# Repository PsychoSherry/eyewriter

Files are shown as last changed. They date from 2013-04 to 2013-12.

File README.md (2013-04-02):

# Eyewriter

A DIY, open-source remote eye tracking toolkit meant to enable artistic digital expression for artists and students with diverse needs. 

This repo contains all of the source files necessary to fabricate and program the electronics system, as well as fabricate an adjustable 3D-printable platform that can be clamped onto any laptop or set on a table.

#### This repo contains:
* 3D files = all of the OpenSCAD scripts (and rendered STLs) for all of the 3D-printable files.
* Arduino sketches = sketches that can be loaded onto the electronics platform.
* BOMs = bills of materials for all required parts for the project.
* Eagle files = design files for all of the electronics modules
* oF app = openFrameworks program to translate camera data into usable actions

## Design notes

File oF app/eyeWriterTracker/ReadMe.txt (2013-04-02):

README 7/20/2010 by ito + kyle
EyeWriter Remote Eye Tracker

To use this realtime eye tracking system, you need a camera and IR LEDs and some electronics hardware.
For information on the hardware, please see (for now):
http://collab.eyewriter.org/?p=123
http://collab.eyewriter.org/?p=102

to use PSEYE USB camera with this software, we recommend to use the newest macam driver.
the macam driver can be downloaded from 
http://sourceforge.net/projects/webcam-osx/files/cvs-build/2009-09-25/macam-cvs-build-2009-09-25.zip/download

Arduino code for driving the hardware is at /StrobeEye/StrobeEye.pde

This software is made with Open Frameworks and based on the original EyeWriter software.
For more information about Open Frameworks and the Eye Writer project please see:
http://www.openframeworks.cc/
http://www.eyewriter.org/

To compile the code, the following openFrameworks addons are needed:
- ofxDirList
- ofxVectorMath
- ofxXmlSettings

Note:

To change the input mode to camera input (movie file input is chosen by default),
change the line 5 of (PROJECT FOLDER)/bin/data/Settings/inputSettings.xml as below.
from:   <mode>1</mode>
to:      <mode>0</mode>

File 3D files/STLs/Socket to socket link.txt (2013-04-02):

 
Cost
Machine time cost is 0.0$.
Material cost is 0.2$.
Total cost is 0.2$.
 
Extent
X axis extrusion starts at -15 mm and ends at 15 mm, for a width of 29 mm.
Y axis extrusion starts at -11 mm and ends at 11 mm, for a depth of 22 mm.
Z axis extrusion starts at 0 mm and ends at 33 mm, for a height of 33 mm.
 
Extruder
Build time is 12 minutes 57 seconds.
Distance extruded is 43078.2 mm.
Distance traveled is 53793.4 mm.
Extruder speed is 40.0
Extruder was extruding 80.1 percent of the time.
Extruder was toggled 4748 times.
Operating flow rate is 7.1 mm3/s.
Feed rate average is 69.2 mm/s, (4152.4 mm/min).
 
Filament
Cross section area is 0.089 mm2.
Extrusion diameter is 0.34 mm.
Volume fraction is 0.82.
 
Material
Mass extruded is 4.1 grams.
Volume extruded is 3.8 cc.
 
Meta
Text has 89122 lines and a size of 3129.0 KB.
Version is 12.03.14
 
Procedures
carve
preface
inset
fill
speed
raft
jitter
comb
cool
dimension
alteration
 
Profile
ABS
 
Slice
Edge width is 0.4 mm.
Layer height is 0.27 mm.

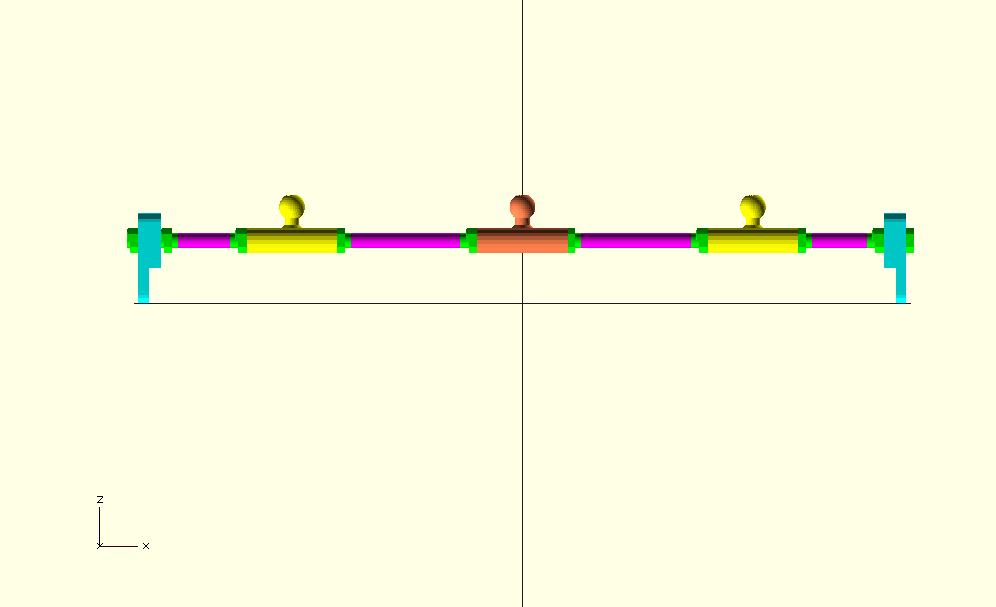
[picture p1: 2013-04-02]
3D files/Full mockup - front.png

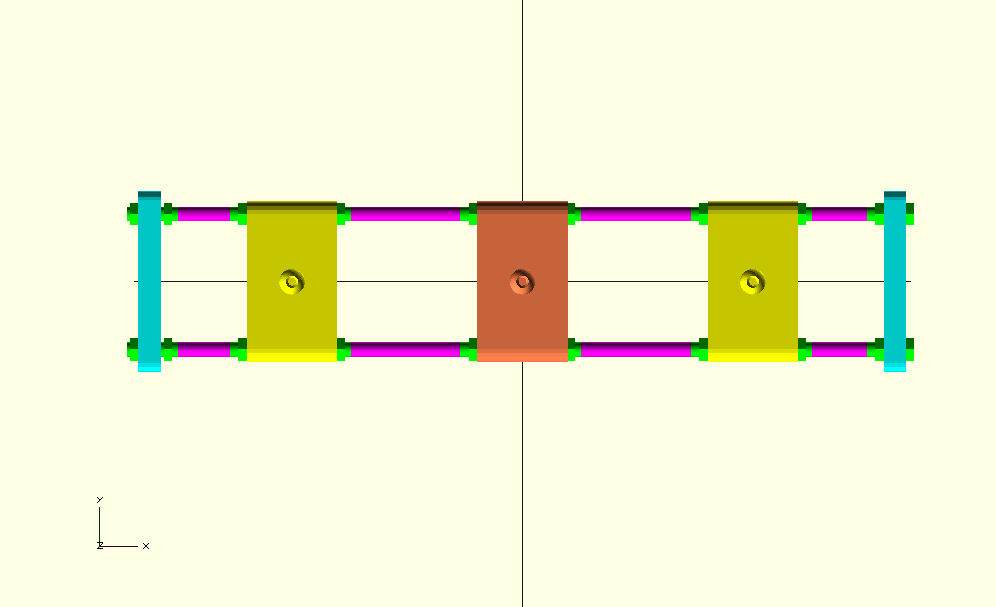
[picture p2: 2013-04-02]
3D files/Full mockup - top.png

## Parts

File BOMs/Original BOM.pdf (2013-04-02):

## Parts List

category | model number | shop | unit price | | total | URL
Camera | PS3Eye | Amazon | $32.00 | 1 | $32 | http://www.amazon.com/PlayStation-Eye-3/dp/B000VTQ3LU
M12 LENS | Board Lens (25 mm) | surveillance-video | $18.00 | 1 | $18 | http://www.surveillance-video.com/bole25mmform.html
M12 LENS holder | cmt-107 | optics-online | $6.00 | 1 | $6.00 | http://www.optics-online.com/
IR Filter | LEE FILTERS 87 100mm x 100mm | B&H (or others) | $13.95 | 1 | $13.95 | http://www.bhphotovideo.com/c/product/102762-REG/LEE_Filters_87P3_3x3_Infra_Red_87.html
IR LED | HSDL-4220 (516-1261-ND) | Digikey | $0.75 | 36 | $27 | http://www.digikey.com/
MOSFET | IRL3714ZPBF (IRL3714ZPBF-ND) | Digikey | $1.41 | 2 | $2.82 | http://www.digikey.com/
Regulator | MC7805ABTG(MC7805ABTGOS-ND) | Digikey | $0.67 | 1 | $0.67 | http://www.digikey.com/
Resistor 3.0OHM 1W | ERX-1SJ3R0 (P3.0W-1BK-ND) | Digikey | less than $1 | 2 | $1.00 | http://www.digikey.com/
Resistor 120OHM 1/4W | ERD-S2TJ121V (P120BACT-ND) | Digikey | less than $1 | 1 | $1.00 | http://www.digikey.com/
Resistor 1kOHM 1/4W | ERD-S2TJ102V (P1.0KBACT-ND) | Digikey | less than $1 | 1 | $1.00 | http://www.digikey.com/
Power Adaptor 7.5V | SPU10-103(7.5V, SPU1010375255595-ND) | Digikey | $14.84 | 1 | $14.84 | http://www.digikey.com/
Transistor | 2N2222 | RadioShack | $0.79 | 1 | $0.79 | http://www.radioshack.com/product/index.jsp?productId=2062608
Potentiometer | Rheostat(25Ohm - 3W) | RadioShack | $3.99 | 2 | $7.98 | http://www.radioshack.com/product/index.jsp?productId=2062299
Arduino | - | SparkFun | $29.95 | 1 | $29.95 | http://www.sparkfun.com/commerce/product_info.php?products_id=666
Male pin for Arduino female pin | Break Away Headers - Straight | SparkFun | $2.50 | 1 | $2.50 | http://www.sparkfun.com/commerce/product_info.php?products_id=116
Visible LED | Red LED | SparkFun | $0.35 | 1 | $0.35 | http://www.sparkfun.com/commerce/product_info.php?products_id=533
USB Cable for Arduino | - | SparkFun | $3.95 | 1 | $3.95 | http://www.sparkfun.com/commerce/product_info.php?products_id=512
BreadBoard | - | SparkFun | $5.95 | 1 | $5.95 | http://www.sparkfun.com/commerce/product_info.php?products_id=9567
Round PCB Kit (5-Pack) | - | RadioShack | $4.99 | 2 | $9.98 | http://www.radioshack.com/product/index.jsp?productId=3173937
Wire | - | RadioShack | $7.69 | 1 | $7.69 | http://www.radioshack.com/product/index.jsp?productId=2062656
Wire(30 Gauge for VSYNC) | - | RadioShack | $3.99 | 1 | $3.99 | http://www.radioshack.com/product/index.jsp?productId=2062642
Solder | thin solder is better.

Soldering Iron

Drill Press

Scissors

Screw Driver

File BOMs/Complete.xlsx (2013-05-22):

R1 | 10k | 0805 | 4 | $0.10 | $0.40 | P10KACT-ND | http://www.digikey.com/product-detail/en/ERJ-6GEYJ103V/P10KACT-ND/43118
R2-R5 | 39ohm | 1W power resistor | 8 | $0.34 | $2.72 | P39W-1BK-ND | http://www.digikey.com/product-detail/en/ERG-1SJ390/P39W-1BK-ND/35788
R6-R8 | 220ohm | 0805 | 3 | $0.10 | $0.30 | P220ACT-ND | http://www.digikey.com/product-detail/en/ERJ-6GEYJ221V/P220ACT-ND/90021
R9 | 100ohm | 0805 | 1 | $0.10 | $0.10 | P100ACT-ND | http://www.digikey.com/product-detail/en/ERJ-6GEYJ101V/P100ACT-ND/21875
R13 | 89ohm | 0805 | 1 | $0.10 | $0.10 | P82ACT-ND | http://www.digikey.com/product-detail/en/ERJ-6GEYJ820V/P82ACT-ND/42830
R14-R15 | 10k | Panel mount pot | 2 | $1.05 | $2.10 | P3A1103-ND | http://www.digikey.com/product-detail/en/EVU-F3AF30B14/P3A1103-ND/243597
C1 | 1uF | 0805 | 1 | $0.10 | $0.10 | 445-3463-1-ND | http://www.digikey.com/product-detail/en/C2012Y5V1H105Z%2F0.85/445-3463-1-ND/1801562
C2-C4 | 0.1uF | 0805 | 3 | $0.10 | $0.30 | 445-7534-1-ND | http://www.digikey.com/product-detail/en/C2012X7R1H104K085AA/445-7534-1-ND/2733606
C5 | 10uF | 1206 | 1 | $0.44 | $0.44 | 493-4147-1-ND | http://www.digikey.com/product-detail/en/F931C106KAA/493-4147-1-ND/2529874
Q1-Q3 | DMN3404L | SOT-23-3 | 3 | $0.45 | $1.35 | DMN3404LDICT-ND | http://www.digikey.com/product-detail/en/DMN3404L-7/DMN3404LDICT-ND/2052805
Q4 | MMBT2222A | SOT-23-3 | 1 | $0.14 | $0.14 | MMBT2222A-FDICT-ND | http://www.digikey.com/product-detail/en/MMBT2222A-7-F/MMBT2222A-FDICT-ND/815723
U1 | ATMEGA328P | 32-TQFP | 1 | $3.05 | $3.05 | ATMEGA328P-AU-ND | http://www.digikey.com/product-detail/en/ATMEGA328P-AU/ATMEGA328P-AU-ND/1832260
Y1 | 16MHz | 3-SMD | 1 | $0.48 | $0.48 | 490-1198-1-ND | http://www.digikey.com/product-detail/en/CSTCE16M0V53-R0/490-1198-1-ND/584635
LED1-LED16 | 940nm IR | 5mm (T 1 3/4) | 32 | $0.36 | $11.56 | 751-1204-ND | http://www.digikey.com/product-detail/en/TSAL6200/751-1204-ND/1681339
LED17 | Green LED | 0805 | 1 | $0.08 | $0.08 | 475-1410-1-ND | http://www.digikey.com/product-detail/en/LG%20R971-KN-1-0-20-R18/475-1410-1-ND/1802598
J1-J2 | 2-pin JST female | SMD R/A | 4 | $0.56 | $2.24 | 455-1749-1-ND | http://www.digikey.com/product-detail/en/S2B-PH-SM4-TB(LF)(SN)/455-1749-1-ND/926846?cur=USD
2-pin JST male plug |  |  | 4 | $0.12 | $0.48 | 455-1592-ND | http://www.digikey.com/product-detail/en/GHR-02V-S/455-1592-ND/807814
26-30AWG crimp contacts |  |  | 8 | $0.11 | $0.88 | 455-1606-1-ND | http://www.digikey.com/product-detail/en/SSHL-002T-P0.2/455-1606-1-ND/1642795
 |  |  |  | Total | $26.82
 |  |  |  |  | 26.82

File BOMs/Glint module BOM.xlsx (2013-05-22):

ID | Value | Package | Qty | Cost | Total | Part number | Source
R1-R2 | 39ohm | 1W power resistor | 2 | $0.34 | $0.68 | P39W-1BK-ND | http://www.digikey.com/product-detail/en/ERG-1SJ390/P39W-1BK-ND/35788
LED1-LED8 | 940nm IR | 5mm (T 1 3/4) | 8 | $0.36 | $2.89 | 751-1204-ND | http://www.digikey.com/product-detail/en/TSAL6200/751-1204-ND/1681339
J1-J2 | 2-pin JST female | SMD R/A | 1 | $0.56 | $0.56 | 455-1749-1-ND | http://www.digikey.com/product-detail/en/S2B-PH-SM4-TB(LF)(SN)/455-1749-1-ND/926846?cur=USD
 |  |  |  | Total | $4.13

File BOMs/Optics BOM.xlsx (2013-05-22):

Name | Specifications | Cost | S&H | Total | Part number | Source
PS3Eye camera | Modified for VSYNC and M12 lenses | $22.00 | $0.00 | $22.00 |  | http://www.amazon.com/Sony-PlayStation-Eye-Camera-Bulk-Packaging/dp/B0072I2240
M12x0.5 mount | 18mm hole spacing | $3.00 | $6.82 | $9.82 |  | http://www.m12lenses.com/Plastic-M12-Lens-Holder-p/pt-lh008p.htm
 | -- or -- 3D-printable | $0.00 | $0.00 | $0.00 |  | http://www.thingiverse.com/thing:83754?save=success
25mm M12 lens |  | $13.23 | $6.38 | $19.61 |  | http://www.m12lenses.com/ProductDetails.asp?ProductCode=PT-2520&CartID=1
IR filter | Band-pass filter (940nm) | $24.00 | $11.20 | $35.20 |  | http://peauproductions.com/store/index.php?main_page=product_info&cPath=2_12&products_id=23
 | -- or -- High-pass filter | $5.00 | $11.20 | $16.20 |  | http://peauproductions.com/store/index.php?main_page=product_info&cPath=2_12&products_id=88
 | -- or -- DIY filter (floppy disk, VHS, exposed film) | $0.00 | $0.00 | $0.00
#000-120x1/4" screws | Only needed for 3D-printed M12 mount. | $6.38 | $0.00 | $6.38 | 92482A147 | McMaster-Carr

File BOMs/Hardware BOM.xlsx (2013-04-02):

Part | Needed | Qty | Cost | P/N | Source
M8 threaded rod | 2 x ~500mm | 1m | $2.27 | 98861A080 | McMaster-Carr
M8 nut | 20 | 100 | $4.51 | 90592A022 | McMaster-Carr
M3 nut | 3 | 100 | $1.04 | 90592A009 | McMaster-Carr
M3x14 bolt | 3 | 100 | $4.24 | 92005A124 | McMaster-Carr
 |  | Total | $12.06

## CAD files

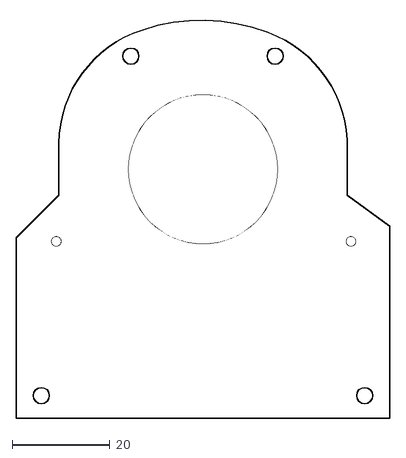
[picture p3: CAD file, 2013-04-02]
3D files/Board outlines/Main-Board.dxf
76.2 x 82.1

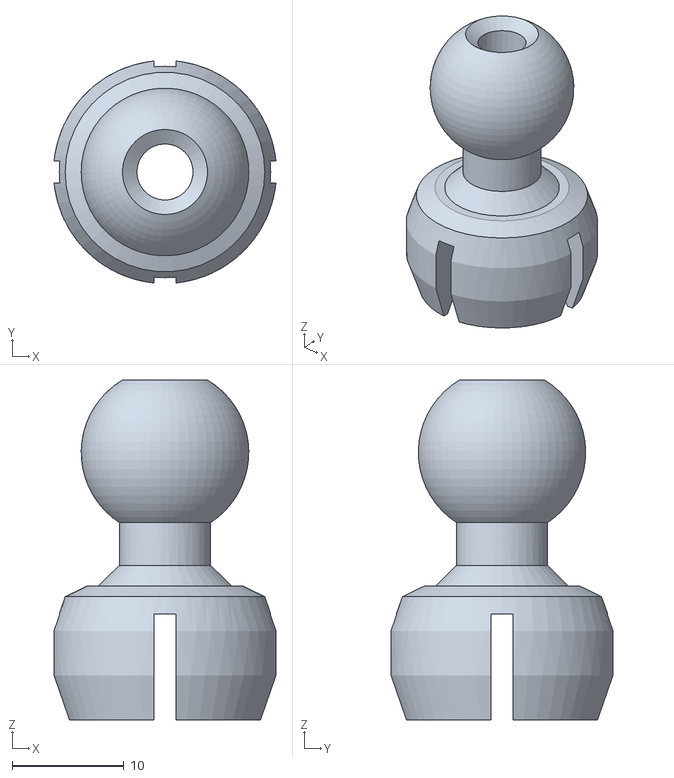
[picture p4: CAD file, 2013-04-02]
3D files/ball-and-socket.stl
19.9 x 19.9 x 30.5

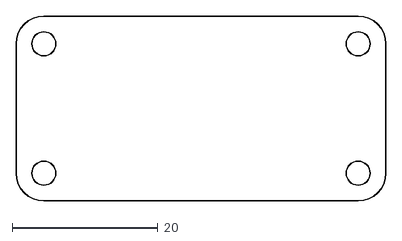
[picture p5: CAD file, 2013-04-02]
3D files/Board outlines/Glint-Module.dxf
50.8 x 25.4

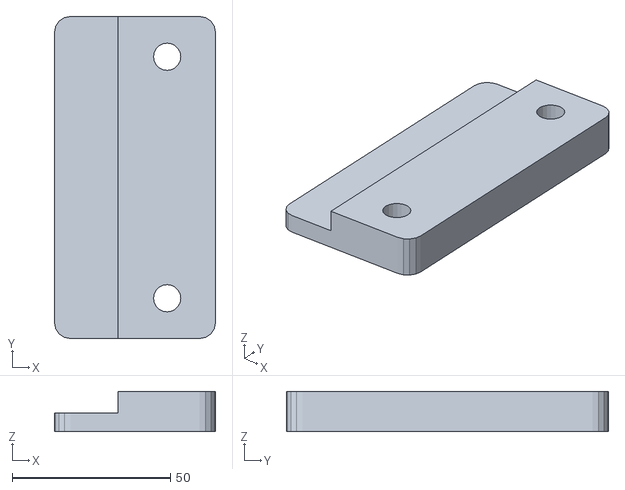
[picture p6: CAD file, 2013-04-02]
3D files/STLs/End block.stl
50.8 x 101.6 x 12.7

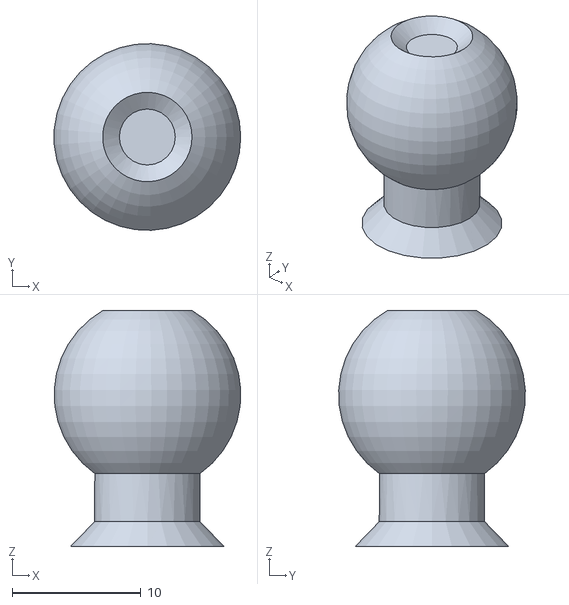
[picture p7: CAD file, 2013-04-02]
3D files/ball.stl
14.5 x 14.5 x 18.3

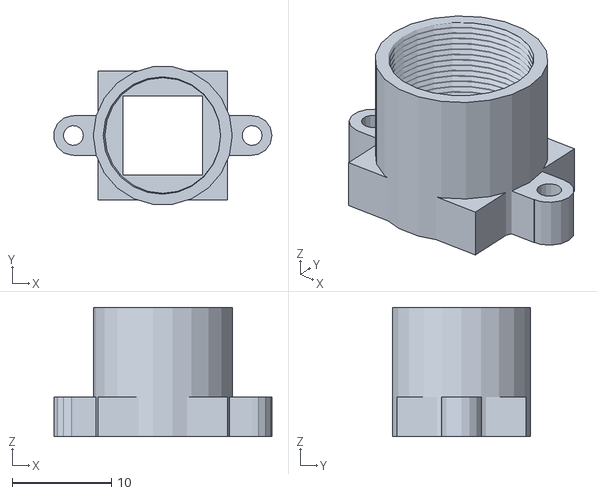
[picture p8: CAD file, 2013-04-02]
3D files/STLs/M12 mount.stl
22.0 x 13.9 x 13.0

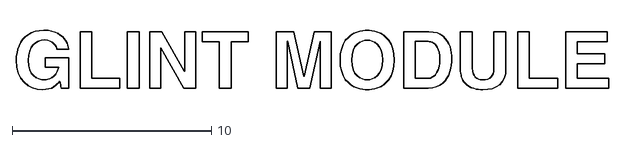
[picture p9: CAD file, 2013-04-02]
3D files/Board outlines/Glint module text.dxf
29.7 x 2.99

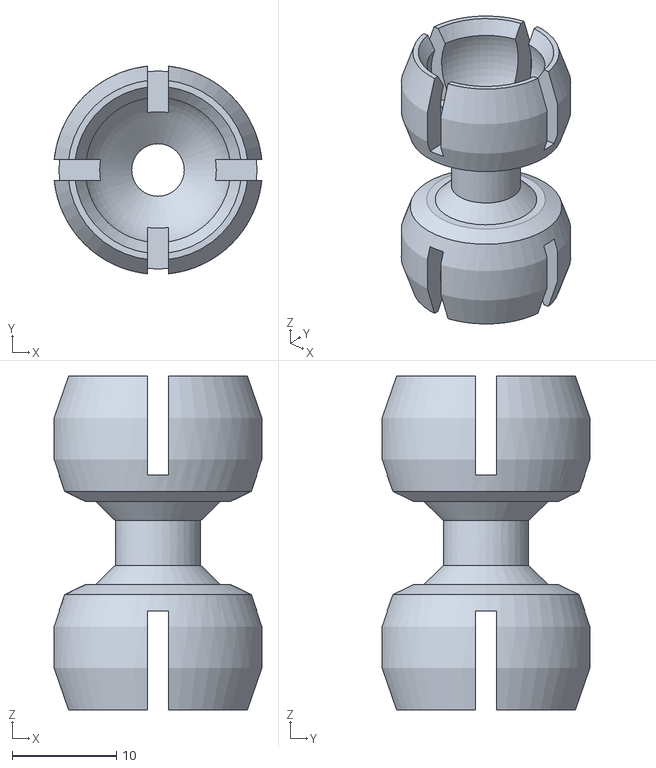
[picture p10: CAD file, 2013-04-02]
3D files/STLs/Socket to socket link.stl
19.9 x 19.9 x 32.0

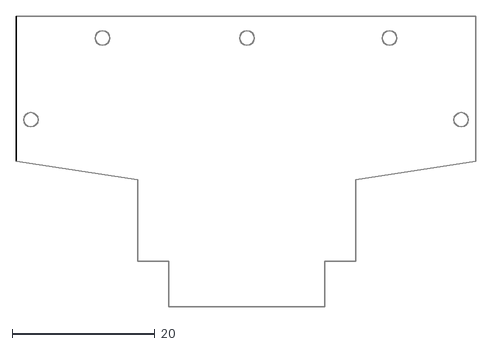
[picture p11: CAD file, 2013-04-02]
3D files/Board outlines/PS3Eye.dxf
64.3 x 40.6

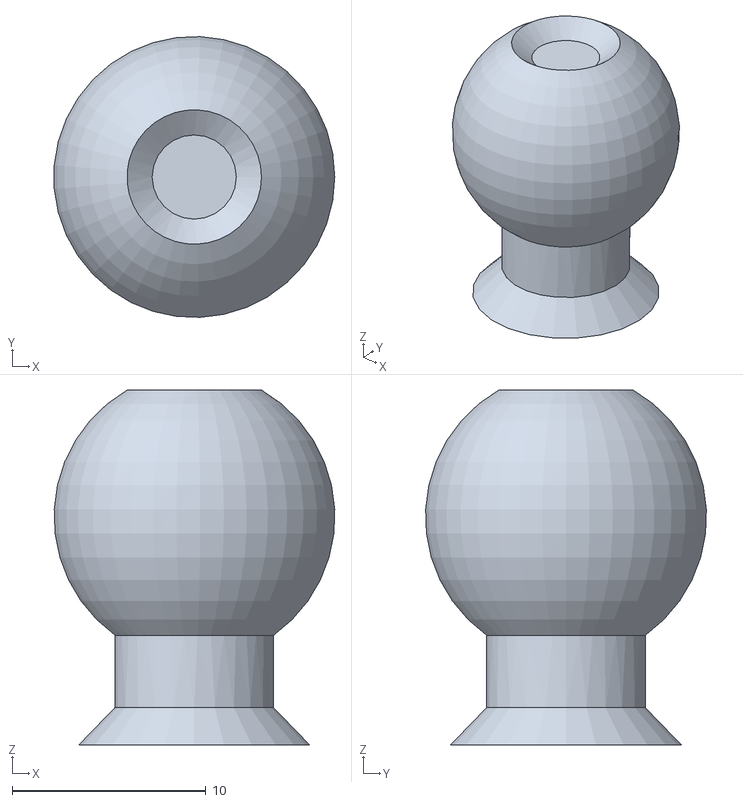
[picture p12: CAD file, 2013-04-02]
3D files/STLs/Modified ball.stl
14.5 x 14.5 x 18.3

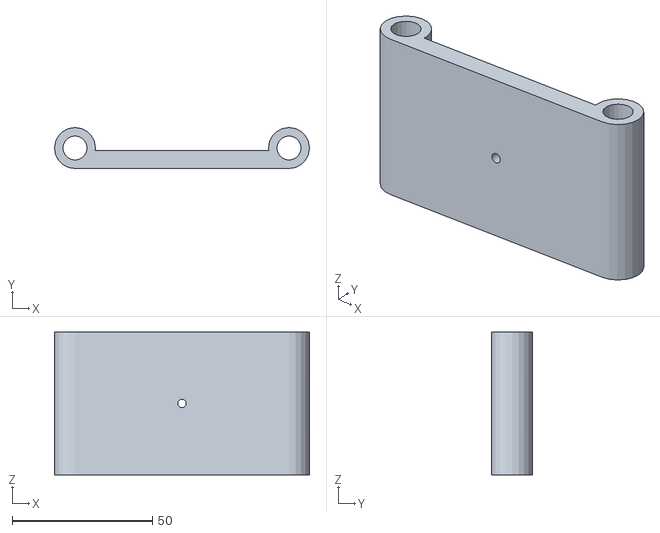
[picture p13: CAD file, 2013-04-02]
3D files/STLs/Platform.stl
90.8 x 14.6 x 50.8

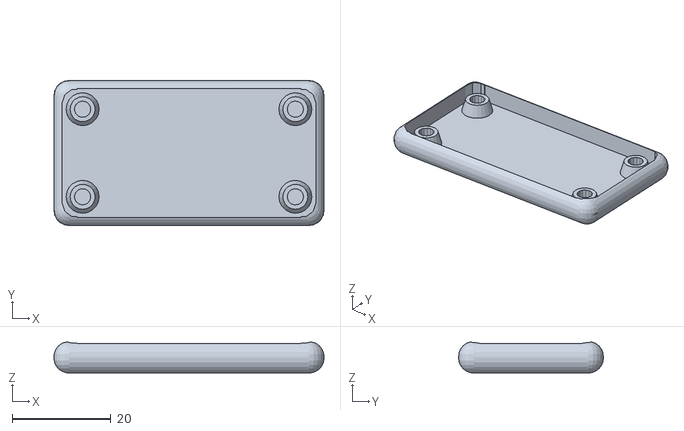
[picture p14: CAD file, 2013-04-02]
3D files/STLs/Glint module housing.stl
54.8 x 29.4 x 6.27

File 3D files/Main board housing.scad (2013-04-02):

include <lib/units.scad>
include <lib/boxes.scad>

housingDepth = 12;

boardWidth = 3*inch;
boardHeight = 3.2*inch;
boardThickness = 1.4;

// Spacer parameters
spacerHeight = .25*inch;
spacerOD = 2;
spacerID = 1;

showMainPCB = false;
showSpacers = true;
showPS3Eye = true;

difference() {
	translate([boardWidth/2, boardHeight/2, housingDepth/2])
		roundedBox([boardWidth + 3, boardHeight + 3, housingDepth], 5, false);
	
	translate([-3,-3,7])
		cube([boardWidth + 5, boardHeight + 5, 5]);

	translate([2.8*inch, 2.5*inch, 0])
		rotate([0,0,180])
			linear_extrude(height = 10)
				import("Board outlines/PS3Eye.dxf");
}

translate([boardWidth/2, boardHeight*2/3 - 3.5, boardThickness])
	color([1,1,1])
		cylinder(r = 12.5, h = 10);


// PS3Eye PCB
module ps3eye() {
	translate([2.8*inch, 2.5*inch, 0])
		rotate([0,0,180])
			linear_extrude(height = boardThickness)
				import("Board outlines/PS3Eye.dxf");
}

// Main PCB
module mainPCB() {
	translate([0,0, spacerHeight + boardThickness]) {
		color([0,1,1]) {
			difference() {
				linear_extrude(height = boardThickness)
					import("Board outlines/Main-Board.dxf");
				
				// Camera lens hole
				translate([1.5*inch, 2*inch, -.1])
					cylinder(r = .6*inch, h = 1.6);
		
				// Left PS3Eye standoff
				translate([.32*inch, 1.42*inch, 0])
					cylinder(r = .0394*inch, h = 1.6, $fn = 15);
		
				// Right PS3Eye standoff
				translate([2.69*inch, 1.42*inch, 0])
					cylinder(r = .0394*inch, h = 1.6, $fn = 15);
			}
		}
	}
}

// Spacers between main board and PS3Eye
module spacers() {
	color([1,0,1]) {
		// Left PCB spacer
		translate([.32*inch, 1.42*inch, boardThickness]) {
			difference() {
				cylinder(r = spacerOD, h = spacerHeight, $fn = 15);
				cylinder(r = spacerID, h = spacerHeight, $fn = 15);
			}
		}
		
		// Right PCB spacer
		translate([2.69*inch, 1.42*inch, boardThickness]) {
			difference() {
				cylinder(r = spacerOD, h = spacerHeight, $fn = 15);
				cylinder(r = spacerID, h = spacerHeight, $fn = 15);
			}
		}
	}
}

if(showMainPCB)		mainPCB();
if(showSpacers)		spacers();
if(showPS3Eye)		ps3eye();

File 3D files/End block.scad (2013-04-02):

include <lib/units.scad>
include <lib/boxes.scad>

block_width = .5*inch;
block_length = 4*inch;
block_height = 2*inch;

hole_size = M8 + 0.6;
hole_distance = 3*inch;

lip_depth = block_width/2;
lip = true;

module generateEndBlock() {
	union() {
		difference() {
			// Rounded block
			translate([0,0,block_width/2])
				roundedBox([block_height, block_length, block_width], 5, true);
	
			// Left hole
			translate([block_height/5, hole_distance/2, block_width/2])
				cylinder(h = block_width + 5, r = hole_size/2, center = true, $fn = 20);
	
			// Right hole
			translate([block_height/5, -hole_distance/2, block_width/2])
				cylinder(h = block_width + 5, r = hole_size/2, center = true, $fn = 20);

			if(lip)
				translate([-block_height/2 + 10, 0, block_width - lip_depth/2])
					cube([20, block_length, lip_depth + 1], center = true);
		}
	}
}

generateEndBlock();

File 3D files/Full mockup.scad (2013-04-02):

include <lib/units.scad>
include <lib/metric_fastners.scad>

// Rod and nut characteristics
rod_length =17*inch;
rod_spacing = 3*inch;
rod_size = 8;
nut_size = 0.8*rod_size;

// Rendering parameters
showRods = true;
showEndBlocks = true;
showGlintPlatforms = true;
showMainPlatform = true;
showNuts = true;

// Colors
rodColor = [1,0,1];
nutColor = [0,1,0];
endBlockColor = [0,1,1];
glintPlatformColor = [1,1,0];
mainPlatformColor = [1,.5,.3];

// Generate all of the nuts for one rod
module generateNuts() {
	translate([-nut_size,rod_spacing/2, 10])
		rotate([0,90,0])
			flat_nut(8);

	translate([0.25*inch+nut_size,rod_spacing/2, 10])
		rotate([0,90,0])
			flat_nut(8);

	translate([rod_length/5 - nut_size - 1*inch,rod_spacing/2, 10])
		rotate([0,90,0])
			flat_nut(8);

	translate([rod_length/5 + 1*inch - 2, rod_spacing/2, 10])
		rotate([0,90,0])
			flat_nut(8);

	translate([rod_length/2 - 1*inch - nut_size, rod_spacing/2, 10])
		rotate([0,90,0])
			flat_nut(8);

	translate([rod_length/2 + 1*inch - 2, rod_spacing/2, 10])
		rotate([0,90,0])
			flat_nut(8);

	translate([4*rod_length/5 - 1*inch - nut_size, rod_spacing/2, 10])
		rotate([0,90,0])
			flat_nut(8);

	translate([4*rod_length/5 + 1*inch - 2, rod_spacing/2, 10])
		rotate([0,90,0])
			flat_nut(8);

	translate([rod_length - 0.25*inch - nut_size*2 , rod_spacing/2, 10])
		rotate([0,90,0])
			flat_nut(8);

	translate([rod_length - 2, rod_spacing/2, 10])
		rotate([0,90,0])
			flat_nut(8);
}

// Generates both of the threaded rods
module generateRods() {
	// Front rod
	translate([-nut_size,-1.5*inch,10])
		rotate([0,90,0])
			cylinder(r = 4, h = rod_length + nut_size*2 - 2);
		
	// Back rod
	translate([-nut_size,1.5*inch,10])
		rotate([0,90,0])
			cylinder(r = 4, h = rod_length + nut_size*2 - 2);
}


// Imports and renders the two end blocks
module generateEndBlocks() {
	// Left end block
	rotate([0,-90,180])
		import("STLs/End block.stl");
	
	// Right end block
	translate([rod_length,0,0])
		rotate([0,-90,0])
			import("STLs/End block.stl");
}

// Imports and renders the glint platforms
module generateGlintPlatforms() {
	// Left glint platform
	union() {
		// Platform
		translate([rod_length/5 + 1*inch,0,10])
			rotate([-90,0,90])
				import("STLs/Platform.stl");
	
		// Nub
		translate([rod_length/5,0,17])
			import("STLs/Modified nub.stl");
	}
	
	// Right glint platform
	union() {
		// Platform
		translate([4*rod_length/5 + 1*inch,0,10])
			rotate([-90,0,90])
				import("STLs/Platform.stl");
	
		// Nub
		translate([4*rod_length/5,0,17])
			import("STLs/Modified nub.stl");
	}
}

// Imports and renders the main platform
module generateMainPlatform() {
	// Main platform
	union() {
		// Platform
		translate([rod_length/2 + 1*inch,0,10])
			rotate([-90,0,90])
				import("STLs/Platform.stl");
	
		// Nub
		translate([rod_length/2,0,17])
			import("STLs/Modified nub.stl");
	}
}

translate([-rod_length/2, 0, 1*inch]) {
	if(showRods)	color(rodColor)	generateRods();
	if(showEndBlocks)	color(endBlockColor)		generateEndBlocks();
	if(showGlintPlatforms)	color(glintPlatformColor)		generateGlintPlatforms();
	if(showMainPlatform)	color(mainPlatformColor)	generateMainPlatform();
	if(showNuts) {
		color(nutColor) {
			generateNuts();
			translate([0,-rod_spacing,0])	generateNuts();
		}
	}
}

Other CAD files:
3D files/Glint module housing.scad
3D files/M12 mount.scad
3D files/Modified nub.scad
3D files/Platform.scad
3D files/Socket to socket link.scad

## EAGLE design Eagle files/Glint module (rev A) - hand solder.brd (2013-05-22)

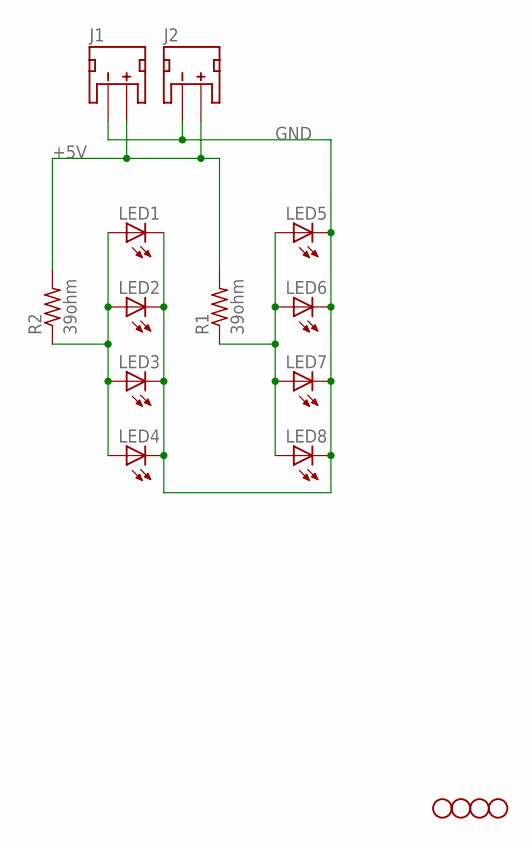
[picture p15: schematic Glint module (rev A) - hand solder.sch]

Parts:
J1, J2: JST_2MM_MALE; JST-2-SMD
LED1, LED2, LED3, LED4, LED5, LED6, LED7, LED8: LED5MM
R1, R2: 39ohm; 0309/10
STANDOFF1, STANDOFF2, STANDOFF3, STANDOFF4: STAND-OFF

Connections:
+5V: J1.2 (+), J2.2 (+), R1.2, R2.2
GND: J1.1 (-), J2.1 (-), LED1.K (C), LED2.K (C), LED3.K (C), LED4.K (C), LED5.K (C), LED6.K (C), LED7.K (C), LED8.K (C)
unnamed: LED1.A, LED2.A, LED3.A, LED4.A, R2.1
unnamed: LED5.A, LED6.A, LED7.A, LED8.A, R1.1

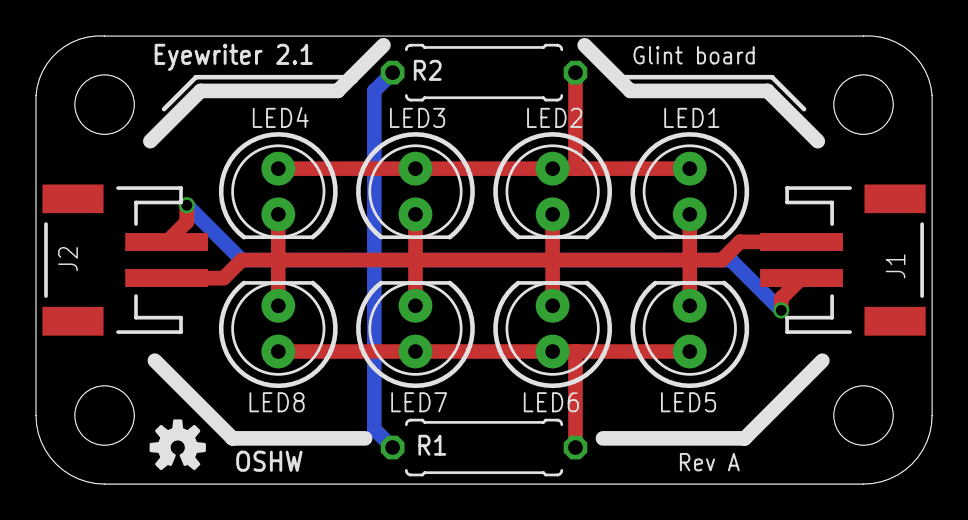
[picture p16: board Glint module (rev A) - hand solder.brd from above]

Board: 2 copper layers, 49.8 x 24.9 mm, 17 parts (0 on the bottom side), 4 nets.

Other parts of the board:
U$1: OSHW-LOGO-S

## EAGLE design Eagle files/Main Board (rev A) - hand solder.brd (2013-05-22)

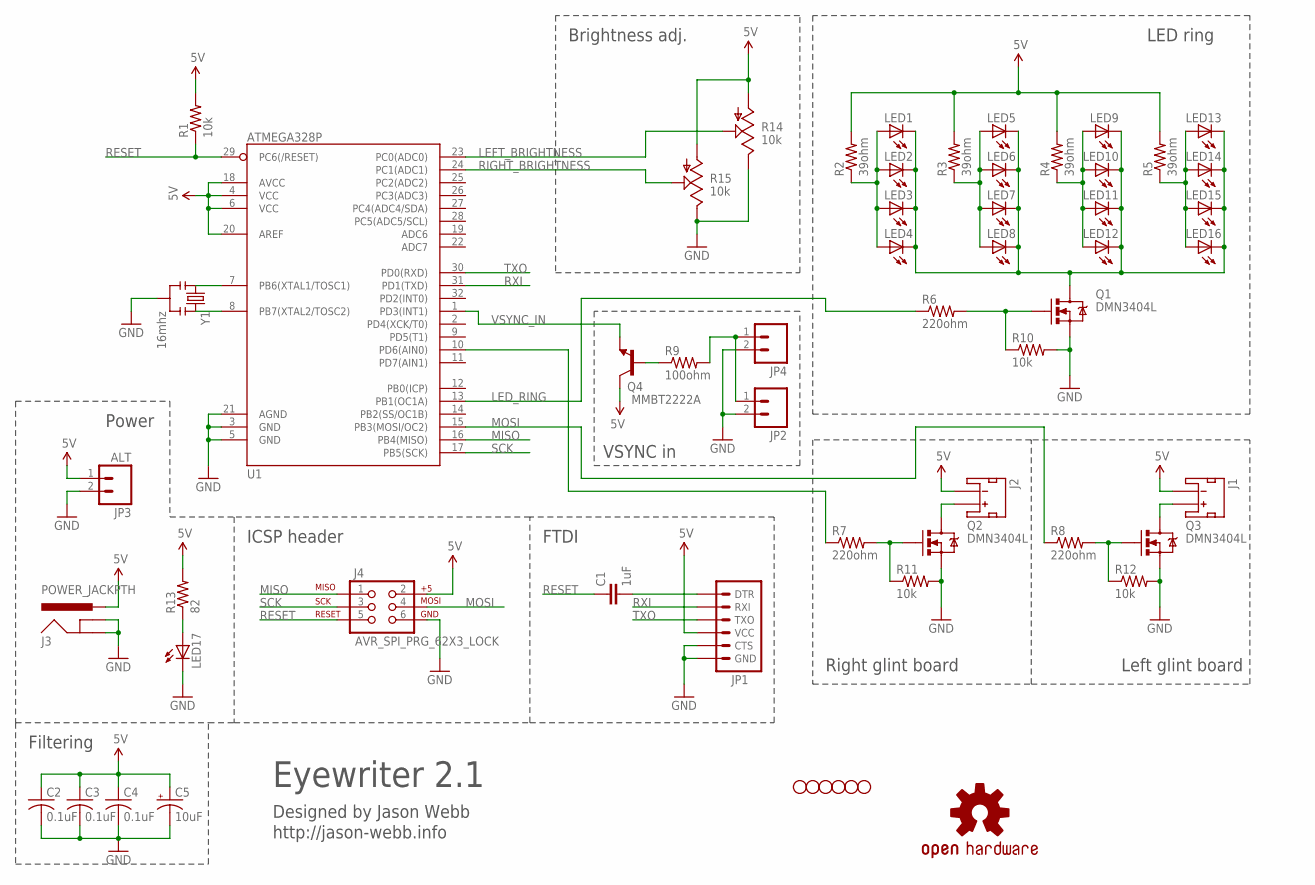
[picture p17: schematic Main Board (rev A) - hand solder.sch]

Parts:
C1: 1uF; 0805
C2, C3, C4: 0.1uF; C0805K
C5: 10uF; A/3216-18R
J1, J2: JST_2MM_MALE; JST-2-SMD
J3: POWER_JACKPTH; POWER_JACK_PTH
J4: AVR_SPI_PRG_62X3_LOCK; 2X3_LOCK
JP1: ARDUINO_SERIAL_PROGRAMLOCK; 1X06_LOCK
JP2, JP4: M02PTH; 1X02
JP3: ALT; 1X02
LED1, LED2, LED3, LED4, LED5, LED6, LED7, LED8, LED9, LED10, LED11, LED12, LED13, LED14, LED15, LED16: LED5MM
LED17: LEDCHIPLED_0805; CHIPLED_0805
LOGO1: OSHW-LOGOS; OSHW-LOGO-S
Q1, Q2, Q3: DMN3404L; SOT23-3
Q4: MMBT2222A; SOT23
R1, R10, R11, R12: 10k; 0805
R2, R3, R4, R5: 39ohm; 0309/10
R6, R7, R8: 220ohm; 0805
R9: 100ohm; 0805
R13: 82; 0805
R14, R15: 10k; ALPS_POT
STANDOFF1, STANDOFF2, STANDOFF3, STANDOFF4, STANDOFF5, STANDOFF6: STAND-OFF
U1: ATMEGA328P; TQFP32-08
Y1: 16mhz; RESONATOR-PTH

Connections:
5V: C2.1, C3.1, C4.1, C5.+, J1.1 (-), J2.1 (-), J3.PWR, J4.2, JP1.4 (VCC), JP3.1, Q4.3 (C), R1.2, R2.2, R3.2, R4.2, R5.2, R13.2, R14.P$3 (A), R15.P$3 (A), U1.4 (VCC), U1.6 (VCC), U1.18 (AVCC), U1.20 (AREF)
GLINT_RIGHT: R8.1, U1.15 (PB3(MOSI/OC2))
GND: C2.2, C3.2, C4.2, C5.-, J3.GND, J3.GNDBREAK, J4.6, JP1.5 (CTS), JP1.6 (GND), JP2.2, JP3.2, JP4.2, LED17.C, Q1.2 (S), Q2.2 (S), Q3.2 (S), R10.2, R11.2, R12.2, R14.P$1 (E), R15.P$1 (E), U1.3 (GND), U1.5 (GND), U1.21 (AGND), Y1.2
LED_RING: R6.1, U1.13 (PB1(OC1A))
LEFT_BRIGHTNESS: R14.P$2 (S), U1.23 (PC0(ADC0))
MISO: J4.1, U1.16 (PB4(MISO))
MOSI: J4.4, R7.1, U1.10 (PD6(AIN0))
unnamed: LED17.A, R13.1
unnamed: U1.7 (PB6(XTAL1/TOSC1)), Y1.1
unnamed: U1.8 (PB7(XTAL2/TOSC2)), Y1.3
unnamed: LED1.A, LED2.A, LED3.A, LED4.A, R2.1
unnamed: J2.2 (+), Q2.3 (D)
unnamed: LED5.A, LED6.A, LED7.A, LED8.A, R3.1
unnamed: Q1.1 (G), R6.2, R10.1
unnamed: LED9.A, LED10.A, LED11.A, LED12.A, R4.1
unnamed: Q2.1 (G), R7.2, R11.1
unnamed: LED13.A, LED14.A, LED15.A, LED16.A, R5.1
unnamed: J1.2 (+), Q3.3 (D)
unnamed: JP2.1, JP4.1, R9.2
unnamed: LED1.K (C), LED2.K (C), LED3.K (C), LED4.K (C), LED5.K (C), LED6.K (C), LED7.K (C), LED8.K (C), LED9.K (C), LED10.K (C), LED11.K (C), LED12.K (C), LED13.K (C), LED14.K (C), LED15.K (C), LED16.K (C), Q1.3 (D)
unnamed: Q3.1 (G), R8.2, R12.1
unnamed: Q4.1 (B), R9.1
unnamed: C1.2, JP1.1 (DTR)
RESET: C1.1, J4.5, R1.1, U1.29 (PC6(/RESET))
RIGHT_BRIGHTNESS: R15.P$2 (S), U1.24 (PC1(ADC1))
RXI: JP1.2 (RXI), U1.31 (PD1(TXD))
SCK: J4.3, U1.17 (PB5(SCK))
TXO: JP1.3 (TXO), U1.30 (PD0(RXD))
VSYNC_IN: Q4.2 (E), U1.1 (PD3(INT1))

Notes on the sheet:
ICSP header
FTDI
LED ring
Right glint board
Left glint board
Brightness adj.
VSYNC in
Power
Eyewriter 2.1
Designed by Jason Webb
http://jason-webb.info
Filtering

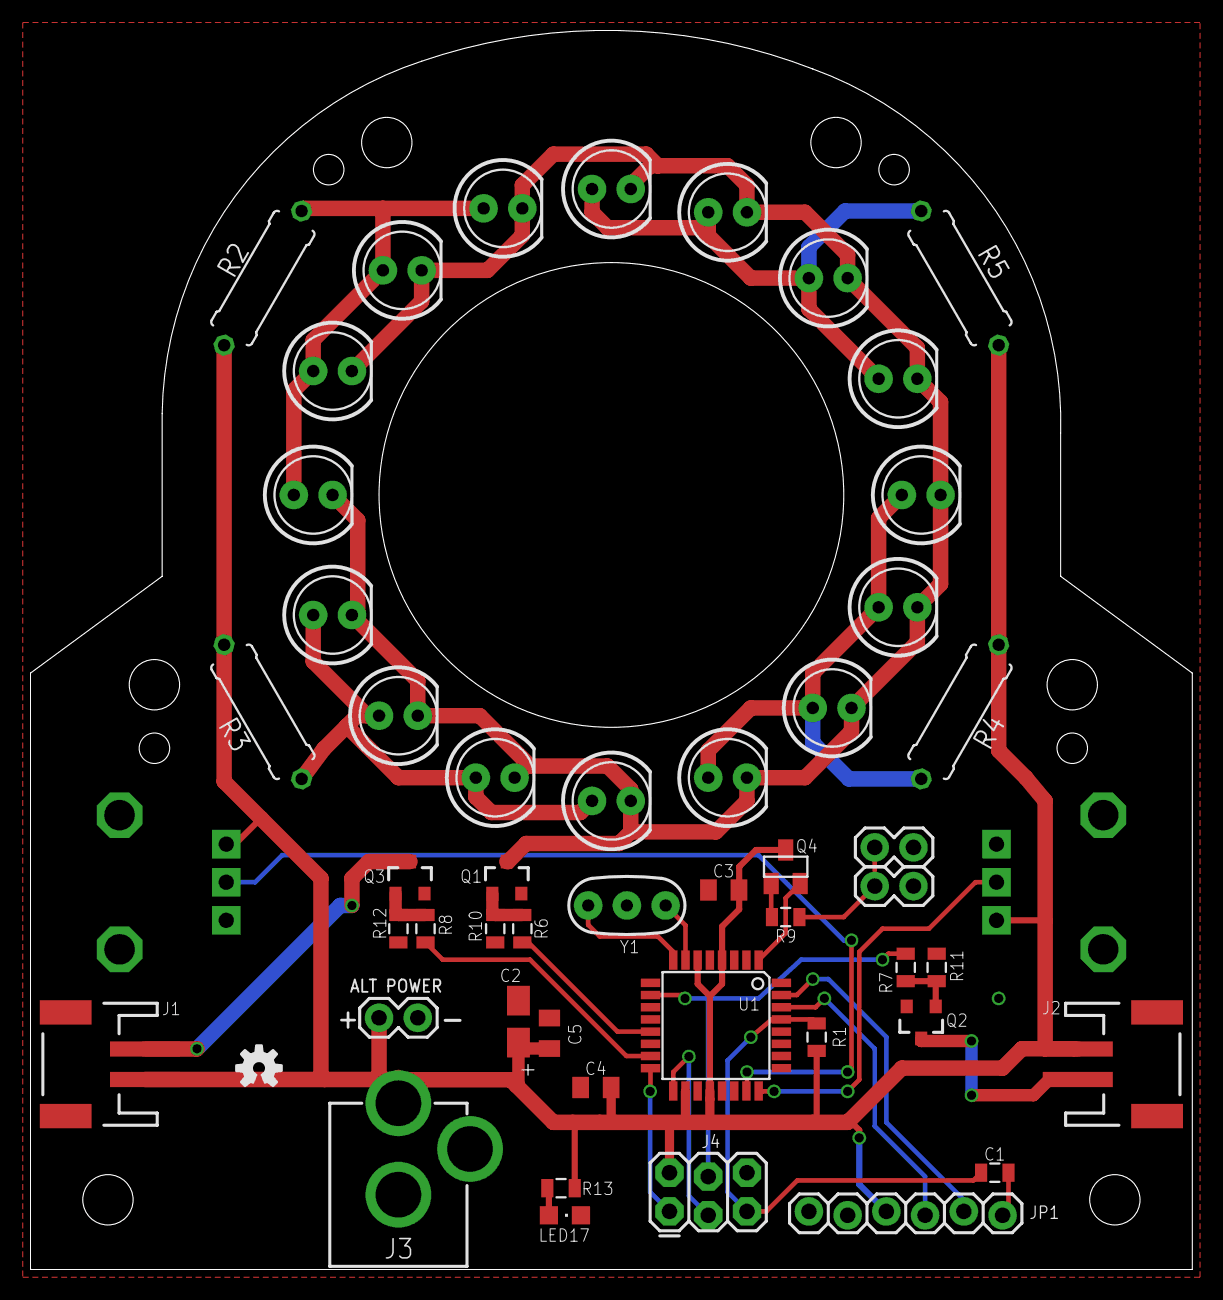
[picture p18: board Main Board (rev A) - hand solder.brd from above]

Board: 2 copper layers, 76.2 x 81.3 mm, 58 parts (0 on the bottom side), 29 nets.

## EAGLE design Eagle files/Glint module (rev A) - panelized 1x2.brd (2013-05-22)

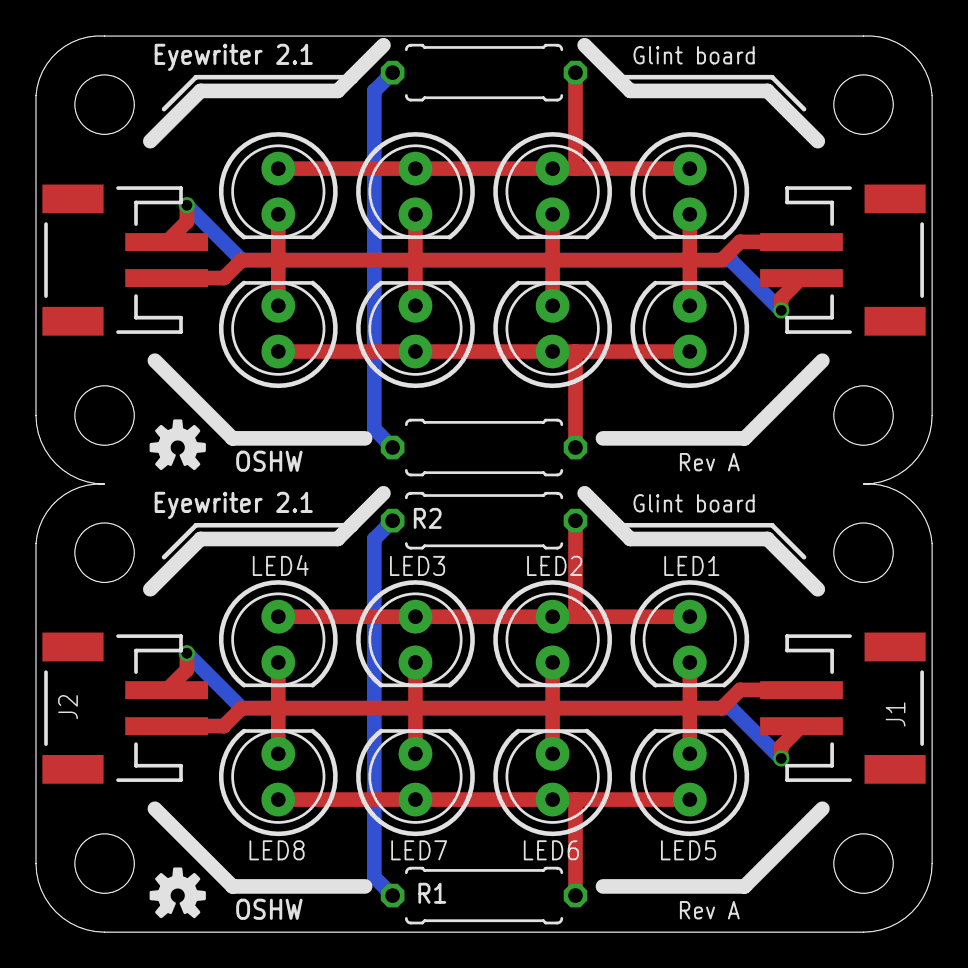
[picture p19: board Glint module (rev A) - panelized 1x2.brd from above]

Board: 2 copper layers, 49.8 x 49.8 mm, 34 parts (0 on the bottom side), 8 nets.

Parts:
J1, J2, J3, J4: JST-2-SMD
LED1, LED2, LED3, LED4, LED5, LED6, LED7, LED8, LED9, LED10, LED11, LED12, LED13, LED14, LED15, LED16: LED5MM
R1, R2, R3, R4: 39ohm; 0309/10
STANDOFF1, STANDOFF2, STANDOFF3, STANDOFF4, STANDOFF5, STANDOFF6, STANDOFF7, STANDOFF8: STAND-OFF
U$1, U$2: OSHW-LOGO-S

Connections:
+5V: J1.2, J2.2, R1.2, R2.2
+5V1: J3.2, J4.2, R3.2, R4.2
GND: J1.1, J2.1, LED1.K, LED2.K, LED3.K, LED4.K, LED5.K, LED6.K, LED7.K, LED8.K
GND1: J3.1, J4.1, LED9.K, LED10.K, LED11.K, LED12.K, LED13.K, LED14.K, LED15.K, LED16.K
unnamed: LED1.A, LED2.A, LED3.A, LED4.A, R2.1
unnamed: LED9.A, LED10.A, LED11.A, LED12.A, R4.1
unnamed: LED5.A, LED6.A, LED7.A, LED8.A, R1.1
unnamed: LED13.A, LED14.A, LED15.A, LED16.A, R3.1

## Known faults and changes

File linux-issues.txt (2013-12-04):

unable to find:
../../../libs/openFrameworksCompiled/project/win_cb/openFrameworksLib.cbp

Should be:
../../../libs/openFrameworksCompiled/project/linux/libopenFrameworks.cbp

Dependency mentioned in files:
../../../libs/openFrameworksCompiled/lib/win_cb/openFrameworksDebug.lib

What I propose:
../../../libs/openFrameworksCompiled/lib/linux/libopenFrameworks.a
or
../../../libs/openFrameworksCompiled/lib/linux/libopenFrameworksDebug.a
(because no libs in that folder)

Check Postbuild steps
from win eye:
xcopy /e /i /y "$(PROJECT_DIR)..\..\..\export\win_cb\*.dll"  "$(PROJECT_DIR)bin"
cmd /c if not exist "$(PROJECT_DIR)bin/data" mkdir "$(PROJECT_DIR)bin/data"

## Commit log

2013-04-02 Major first commit
    [Arduino pin mapping table.xlsx, End block.scad, End block.stl, Full mockup.scad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]
2013-05-01 Updated Eagle files, including Gerbers and custom library
    [Glint-Module.brd, Main-Board.brd, Main-Board.sch]
2013-05-22 Updated Eagle files + BOMs
    [Complete.xlsx, Glint module BOM.xlsx, Glint-Module.brd, Interconnects BOM.xlsx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]
2013-05-22 Updated Eagle files
    [Glint module (rev A) - hand solder.brd, Glint module (rev A) - hand solder.sch, Glint module (rev A) - panelized 1x2.brd, Main Board (rev A) - hand solder.brd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]
2013-05-29 Removing files
    [Glint-Module.brd]

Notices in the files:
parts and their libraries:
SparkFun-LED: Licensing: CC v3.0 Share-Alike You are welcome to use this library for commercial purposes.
